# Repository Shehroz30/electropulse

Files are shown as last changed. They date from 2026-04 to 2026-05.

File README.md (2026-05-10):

# Electropulse

A custom, homemade, low voltage, simple TENs device
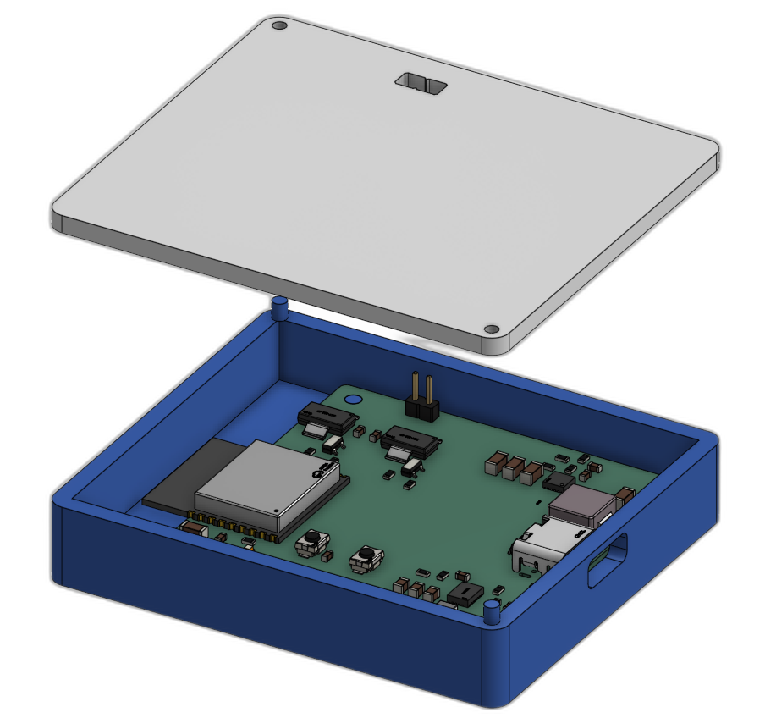
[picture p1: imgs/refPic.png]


## Features
* ESP32-C3 Microntroller with Bluetooth
* Wireless control
* WiFi controlled
* USB-C powered
* Low-cost - total BOM + board ~$11.56 per board
* Two output channels
* Modular + fits with different electrode types
* Two buck boosts for efficiency
* BJT controlled current limiter

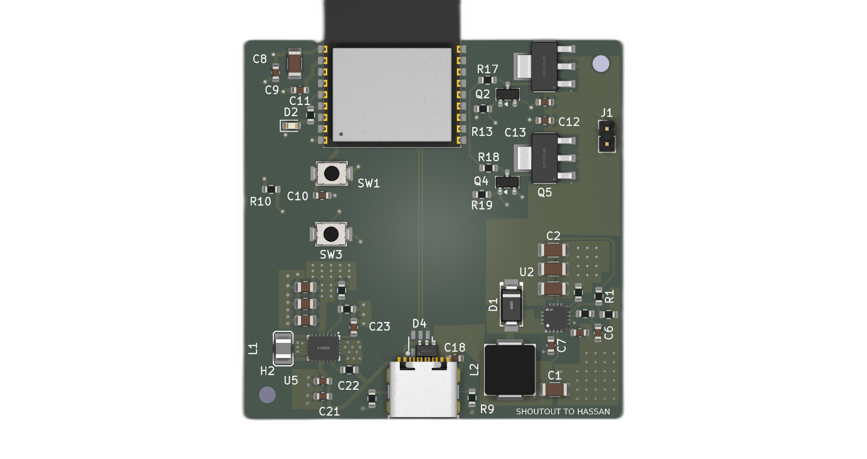
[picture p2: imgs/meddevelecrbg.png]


## Build
The build of this device is extremely uncomplicated. Use M3 0.5 inch screws for the enclosure and M2 0.315 inch screws for mounting the PCB. The electrodes can simply be attached to the Pin Headers.

A link to the Onshape file can be found [here](https://cad.onshape.com/documents/0b9b685ed737be4511598f4a/w/ba1d33f46afe7a8ff807ef53/e/736e59d6b3c7b8673a0b7fd8?renderMode=0&uiState=69ea24d6e717aaec3b4bf4c2)

## Use
* Flash the code onto the ESP32 using Arduino IDE
* Go to http://\<ESP-32\_IP\>/
* Connect your electrodes to the pin headers

## Motivation
I made this project because I've been struggling a little bit with knee pain and I found that other options on the market weren't as adjustable. I also had electrodes lying around (due to a separate business pitch project) and I wanted to make use of them

## BOM
To use this device, electrodes are a requirement. To purchase these, you can go to Amazon at [this link](https://www.amazon.com/Best-Sellers-Electrodes/zgbs/industrial/3013606011)
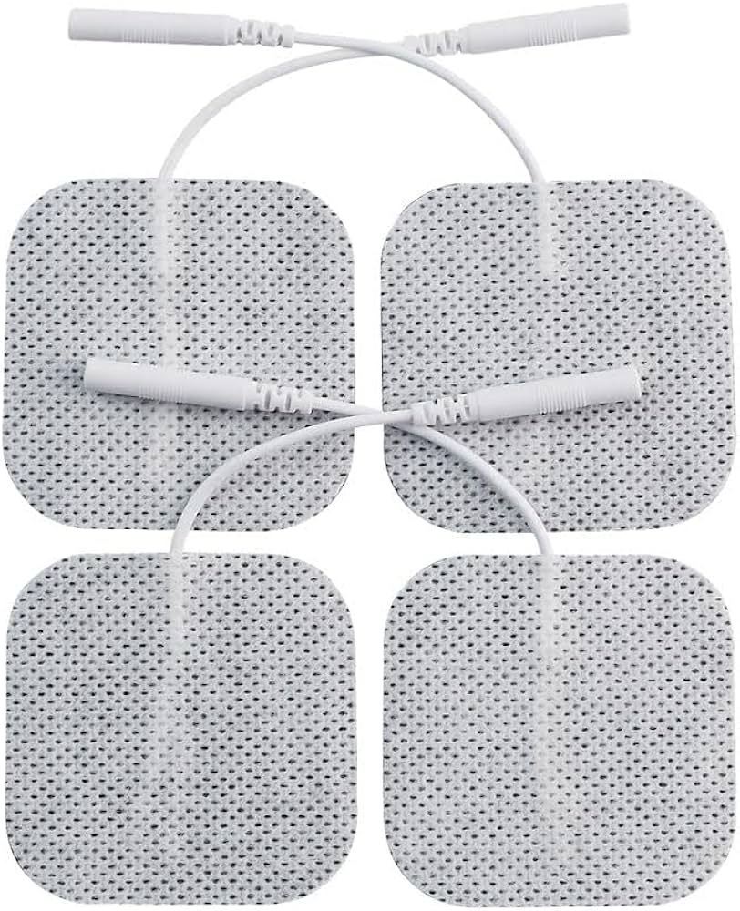
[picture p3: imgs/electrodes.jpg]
Electrodes


| Designator               | Footprint       |   Quantity | Value                | LCSC Part   | Link                                               |
|:-------------------------|:----------------|-----------:|:---------------------|:------------|:---------------------------------------------------|
| C1,C2,C3,C4              | 1206            |          8 | 4.7uF                | C29823      | https://www.lcsc.com/product-detail/C29823.html    |
| C5                       | 0603            |          2 | 0.047uF              | C1622       | https://www.lcsc.com/product-detail/C1622.html     |
| C8                       | 1206            |          2 | 10uF                 | C13585      | https://www.lcsc.com/product-detail/C13585.html    |
| C10,C11,C12,C13,C6,C7,C9 | 0603            |         18 | 0.1uF                | C14663      | https://www.lcsc.com/product-detail/C14663.html    |
| C18,C23                  | 0603            |        4   | 100nf                | C14663      | https://www.lcsc.com/product-detail/C14663.html    |
| C21,C22                  | 0605            |          4 | 10uf                 | C19702      | https://www.lcsc.com/product-detail/C19702.html    |
| C25,C26,C27              | 0805            |          6 | 22uf                 | C45783      | https://www.lcsc.com/product-detail/C45783.html    |
| D1                       | SMA(DO-214AC)   |          2 | D_Schottky           | C8678       | https://www.lcsc.com/product-detail/C8678.html     |
| D2                       | 0603            |          2 | LED                  | C2290       | https://www.lcsc.com/product-detail/C2290.html     |
| D4                       | SOT-23-6L       |          5 | USBLC6-2SC6          | C7519       | https://www.lcsc.com/product-detail/C7519.html     |
| J1                       | 插件,P=2.54mm     |          4 | Conn_01x02           | C32713268   | https://www.lcsc.com/product-detail/C32713268.html |
| J5                       | SMD             |          5 | MC-311D              | C136423     | https://www.lcsc.com/product-detail/C136423.html   |
| L1                       | 1008            |          5 | 2.2uH                | C86092      | https://www.lcsc.com/product-detail/C86092.html    |
| L2                       | SMD,7.2x6.6mm   |          5 | 10uH                 | C5189958    | https://www.lcsc.com/product-detail/C5189958.html  |
| Q2,Q4                    | SOT-23          |         10 | MMBT2222A            | C7420351    | https://www.lcsc.com/product-detail/C7420351.html  |
| Q3,Q5                    | SOT-223         |          5 | FZT853TA             | C435890     | https://www.lcsc.com/product-detail/C435890.html   |
| R1                       | 0603            |          2 | 250k                 | C22961      | https://www.lcsc.com/product-detail/C22961.html    |
| R2                       | 0603            |          2 | 330                  | C23138      | https://www.lcsc.com/product-detail/C23138.html    |
| R6                       | 0603            |          2 | 75k                  | C23242      | https://www.lcsc.com/product-detail/C23242.html    |
| R7                       | 0603            |          2 | 2k                   | C22975      | https://www.lcsc.com/product-detail/C22975.html    |
| R10,R14,R3               | 0603            |          6 | 10k                  | C25804      | https://www.lcsc.com/product-detail/C25804.html    |
| R11,R9                   | 0603            |          4 | 5.1k                 | C23186      | https://www.lcsc.com/product-detail/C23186.html    |
| R13,R19                  | 0603            |          4 | 14                   | C22950      | https://www.lcsc.com/product-detail/C22950.html    |
| R15                      | 0603            |          2 | 1M                   | C22935      | https://www.lcsc.com/product-detail/C22935.html    |
| R16                      | 0603            |         20 | 180k                 | C22827      | https://www.lcsc.com/product-detail/C22827.html    |
| R17,R18                  | 0603            |          4 | 1K                   | C21190      | https://www.lcsc.com/product-detail/C21190.html    |
| SW1,SW3                  | SMD,4x3mm       |          4 | TS-1088-AR02016      | C720477     | https://www.lcsc.com/product-detail/C720477.html   |
| U1                       | VFQFN-32-EP     |          2 | ESP32-C3-WROOM-02-N4 | C2934560    | https://www.lcsc.com/product-detail/C2934560.html  |
| U2                       | WQFN-16-EP(3x3) |          2 | TPS55340RTER         | C169167     | https://www.lcsc.com/product-detail/C169167.html   |
| U5                       | VSON-14-EP(3x4) |          2 | TPS63020DSJR         | C15483      | https://www.lcsc.com/product-detail/C15483.html    |

## JLCBPCB Order
For two assembled PCBs, the cost is around ~70$ for the cheapest shipping option. Keep in mind that there are a lot of alternatives to the parts selected, so ifsomething is unavailable you can easily change them around within the JLCPCB assembly order.
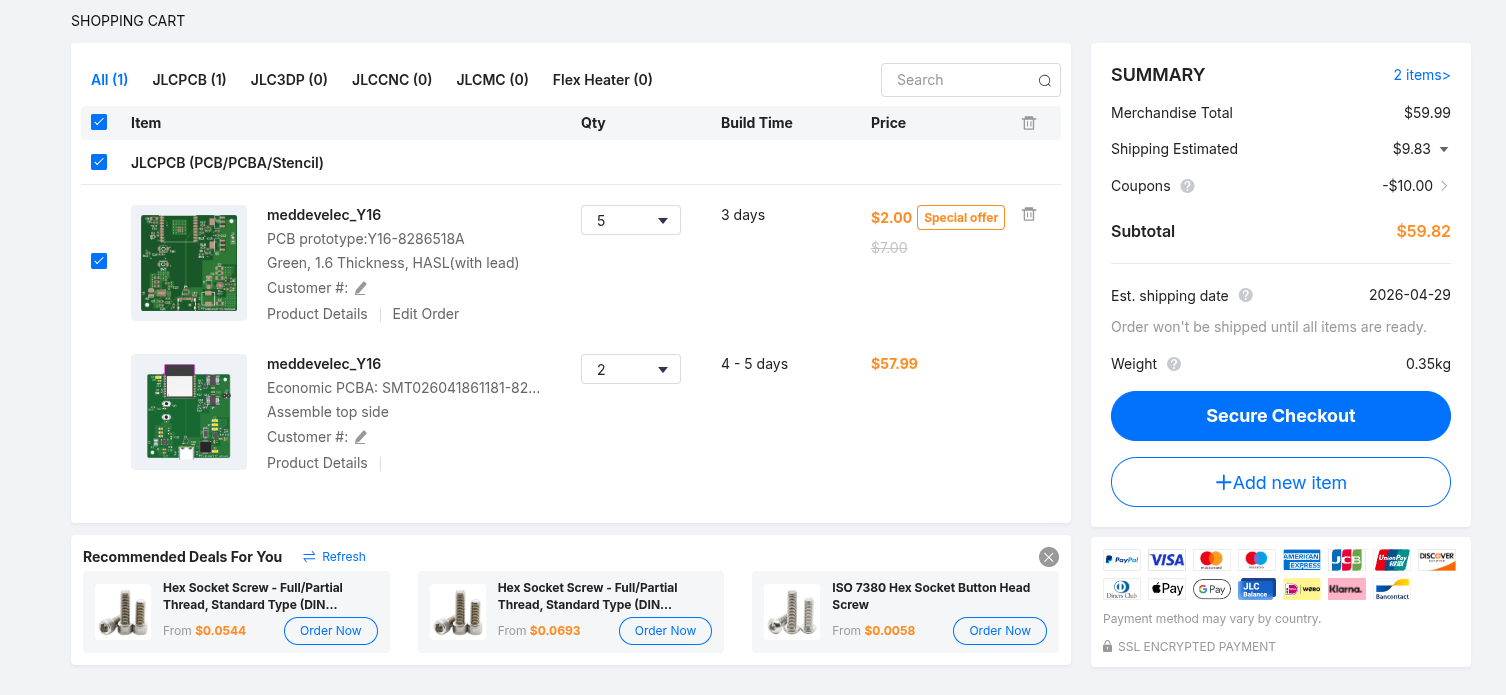
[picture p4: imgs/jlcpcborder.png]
Order


## Firmware

The code is written using Arduino IDE compiled for an ESP32-C3. Please note that the local host where the web page is hosted depends entirely on your ESP32, so it may not be the same for everyone. Also be sure to input your wifi credentials when flashing so that the ESP32 can connect to WiFi. 

## Fallout Zine Poster

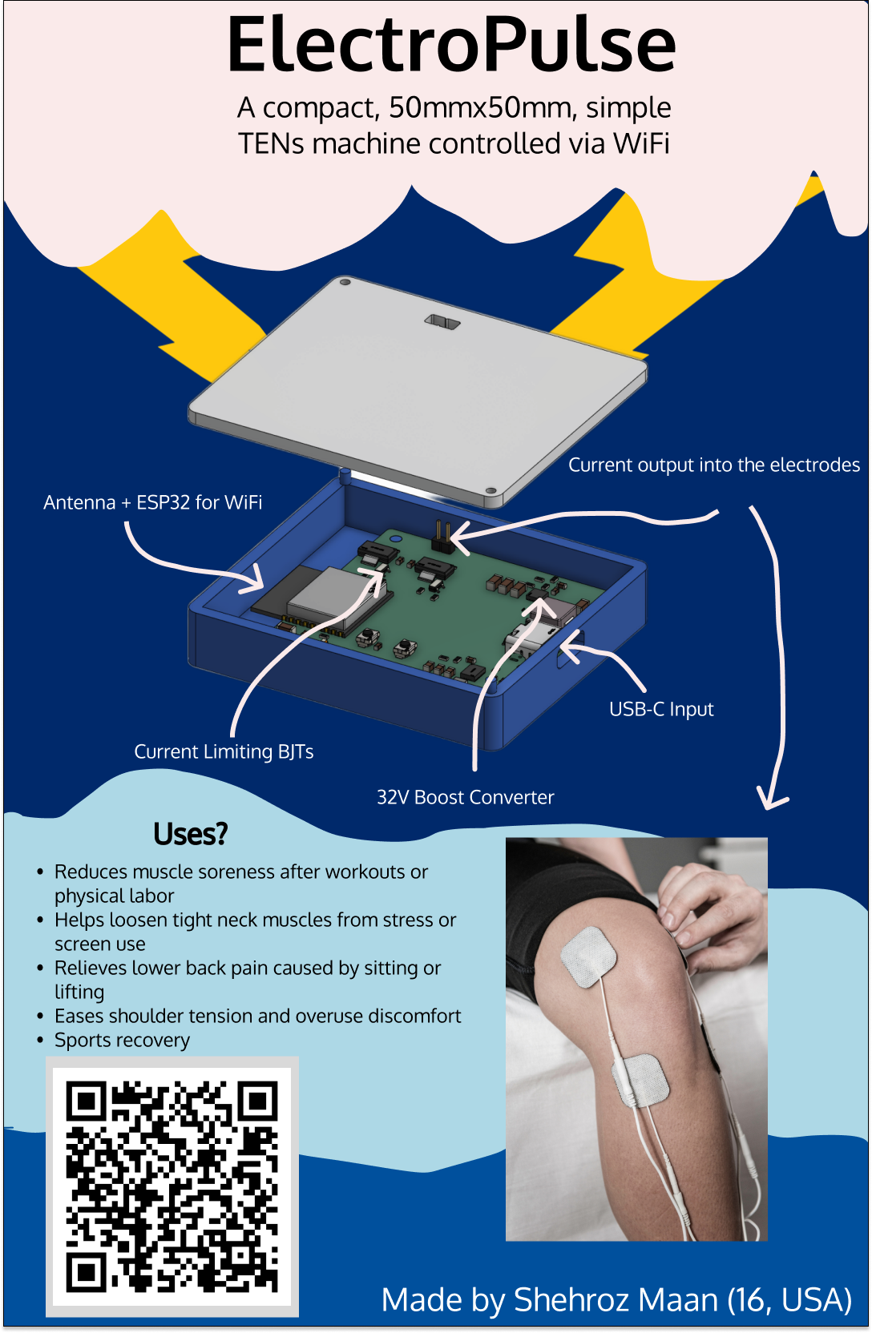
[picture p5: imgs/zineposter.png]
Zine Poster


## Thanks

Huge thanks to HackClub for helping me with this project!

## Verfication
Hack Club Username: shehrozmaan4

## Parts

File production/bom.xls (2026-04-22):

JLCPCB BOM Tool - BOM Matching
BOM name：medtechprojbo-JLCPCB Assembly Order.xlsx |  |  | Download Time：2026-04-19 00:56:08 |  |  |  | * Our matching results are updated in real-time, but stock and prices may change. If it's been over 24 hours, please re-match before placing your order.
PCB Assembled Qty：5 |  |  | Est. Total Price：18.6243
Your BOM |  |  |  |  | Matched Parts |  |  |  |  |  |  | Order Information
Top Designator | Bottom Designator | Comment | Footprint | JLCPCB Part # | Matches | Part # | Manufacturer | Footprint | Description | Category | Warning | JLCPCB Part # | Product link | Lib Type | Qty | Source | Total Price ($)
C1,C2,C3,C4 |  | 4.7uF | 1206 |  | Select by System | 1206B475K500NT | FH (Guangdong Fenghua Advanced Tech) | 1206 | 4.7uF 50V X7R ±10% 1206 Multilayer Ceramic Capacitors MLCC - SMD/SMT ROHS | Multilayer Ceramic Capacitors MLCC - SMD/SMT |  | C29823 | https://jlcpcb.com/partdetail/30577-1206B475K500NT/C29823 | Basic | 8 | 8 JLCPCB | 0.3152
C5 |  | 0.047uF | 0603 |  | Select by System | CL10B473KB8NNNC | Samsung Electro-Mechanics | 0603 | 47nF 50V X7R ±10% 0603 Multilayer Ceramic Capacitors MLCC - SMD/SMT ROHS | Multilayer Ceramic Capacitors MLCC - SMD/SMT |  | C1622 | https://jlcpcb.com/partdetail/1974-CL10B473KB8NNNC/C1622 | Basic | 2 | 2 JLCPCB | 0.0106
C8 |  | 10uF | 1206 |  | Select by System | CL31A106KBHNNNE | Samsung Electro-Mechanics | 1206 | 10uF 50V X5R ±10% 1206 Multilayer Ceramic Capacitors MLCC - SMD/SMT ROHS | Multilayer Ceramic Capacitors MLCC - SMD/SMT |  | C13585 | https://jlcpcb.com/partdetail/14236-CL31A106KBHNNNE/C13585 | Basic | 2 | 2 JLCPCB | 0.1244
C10,C11,C12,C13,C6,C7,C9 |  | 0.1uF | 0603 |  | Unconfirmed | CC0603KRX7R9BB104 | YAGEO | 0603 | 100nF 50V X7R ±10% 0603 Multilayer Ceramic Capacitors MLCC - SMD/SMT ROHS | Multilayer Ceramic Capacitors MLCC - SMD/SMT | 1.Multiple lines in the BOM have been matched to the same part. Please check if the matching is correct. ; | C14663 | https://jlcpcb.com/partdetail/YAGEO-CC0603KRX7R9BB104/C14663 | Basic | 18 | 18 JLCPCB | 0.0558
C18,C23 |  | 100nf | 0603 |  | Unconfirmed | CC0603KRX7R9BB104 | YAGEO | 0603 | 100nF 50V X7R ±10% 0603 Multilayer Ceramic Capacitors MLCC - SMD/SMT ROHS | Multilayer Ceramic Capacitors MLCC - SMD/SMT | 1.Multiple lines in the BOM have been matched to the same part. Please check if the matching is correct. ; | C14663 | https://jlcpcb.com/partdetail/YAGEO-CC0603KRX7R9BB104/C14663 | Basic | 18 | 18 JLCPCB | 0.0558
C21,C22 |  | 10uf | 0603 |  | Select by System | CL10A106KP8NNNC | Samsung Electro-Mechanics | 0603 | 10V 10uF X5R ±10% 0603 Multilayer Ceramic Capacitors MLCC - SMD/SMT ROHS | Multilayer Ceramic Capacitors MLCC - SMD/SMT |  | C19702 | https://jlcpcb.com/partdetail/20411-CL10A106KP8NNNC/C19702 | Basic | 4 | 4 JLCPCB | 0.032
C25,C26,C27 |  | 22uf | 0805 |  | Select by System | CL21A226MAQNNNE | Samsung Electro-Mechanics | 0805 | 22uF 25V X5R ±20% 0805 Multilayer Ceramic Capacitors MLCC - SMD/SMT ROHS | Multilayer Ceramic Capacitors MLCC - SMD/SMT |  | C45783 | https://jlcpcb.com/partdetail/46786-CL21A226MAQNNNE/C45783 | Basic | 6 | 6 JLCPCB | 0.1914
D1 |  | D_Schottky | SMA(DO-214AC) |  | Select by System | SS34 | MDD(Microdiode Semiconductor) | SMA(DO-214AC) | -55℃~+125℃ 3A 40V 500uA@40V 550mV@3A Independent SMA(DO-214AC) Schottky Diodes ROHS | Schottky Diodes |  | C8678 | https://jlcpcb.com/partdetail/MDD_Microdiode_Semiconductor-SS34/C8678 | Basic | 2 | 2 JLCPCB | 0.0596
D2 |  | LED | 0603 |  | Select by System | KT-0603W | Hubei KENTO Elec | 0603 | -40℃~+85℃ 100mW 120° 2.6V~3.1V 360mcd 5mA Discrete Diode Top-mount White Yellow Lens 0603 LED Indication - Discrete ROHS | LED Indication - Discrete |  | C2290 | https://jlcpcb.com/partdetail/Hubei_KENTOElec-KT0603W/C2290 | Basic | 2 | 2 JLCPCB | 0.024
D4 |  | USBLC6-2SC6 | SOT-23-6L |  | Select by System | USBLC6-2SC6 | STMicroelectronics | SOT-23-6L | -40℃~+125℃ 150nA 17V 2 3.5pF 5.25V 5A 6V ESD IEC 61000-4-2 Unidirectional SOT-23-6L ESD and Surge Protection (TVS/ESD) ROHS | ESD And Surge Protection (TVS/ESD) |  | C7519 | https://jlcpcb.com/partdetail/STMicroelectronics-USBLC62SC6/C7519 | Extended | 5 | 5 JLCPCB | 0.7245
J1 |  | Conn_01x02 | 插件,P=2.54mm |  | Select by System | HX PZ2.54-1x2P ZZ | hanxia | 插件,P=2.54mm | -40℃~+105℃ 1 1kV 1x2P 2.54mm 2.5mm 2P 3A 3mm 6mm Black Brass Gold Pin Header Through Hole Plugin,P=2.54mm Pin Headers ROHS | Pin Headers |  | C32713268 | https://jlcpcb.com/partdetail/hanxia-HX_PZ2_54_1x2PZZ/C32713268 | Extended | 4 | 4 JLCPCB | 0.0628
J5 |  | MC-311D | SMD |  | Select by System | MC-311D | SOFNG | SMD | -35℃~+75℃ 1 12V 16P 5A 7.35mm 8,000 times、10000 times Black Female Surface Mount, Right Angle Type-C SMD USB Connectors ROHS | USB Connectors |  | C136423 | https://jlcpcb.com/partdetail/SOFNG-MC311D/C136423 | Extended | 5 | 5 JLCPCB | 1.1375
L1 |  | 2.2uH | 1008 |  | Select by System | LQM2HPN2R2MG0L | Murata Electronics | 1008 | 1.3A 100mΩ 2.2uH 40MHz ±20% 1008 Inductors (SMD) ROHS | Inductors (SMD) |  | C86092 | https://jlcpcb.com/partdetail/MurataElectronics-LQM2HPN2R2MG0L/C86092 | Extended | 5 | 5 JLCPCB | 0.4515
L2 |  | 10uH | SMD,7.2x6.6mm |  | Select by System | CYA0630-10UH | SHOU HAN | SMD,7.2x6.6mm | 10uH 4A 5.5A 71mΩ ±20% SMD,7.2x6.6mm Inductors (SMD) ROHS | Inductors (SMD) |  | C5189958 | https://jlcpcb.com/partdetail/SHOUHAN-CYA063010UH/C5189958 | Extended | 5 | 5 JLCPCB | 0.763
Q2,Q4 |  | MMBT2222A | SOT-23 |  | Select by System | MMBT2222A | hongjiacheng | SOT-23 | -55℃~+150℃ 1 NPN 100 100nA 1V 300MHz 300mW 40V 600mA 6V NPN SOT-23 Bipolar (BJT) ROHS | Bipolar (BJT) |  | C7420351 | https://jlcpcb.com/partdetail/hongjiacheng-MMBT2222A/C7420351 | Extended | 10 | 10 JLCPCB | 0.152
Q3,Q5 |  | FZT853TA | SOT-223 |  | Select by System | FZT853TA | Diodes Incorporated | SOT-223 | -55℃~+150℃ 1 NPN 100 100V 10nA 130MHz 150mV 3W 6A 7V NPN SOT-223 Bipolar (BJT) ROHS | Bipolar (BJT) |  | C435890 | https://jlcpcb.com/partdetail/DiodesIncorporated-FZT853TA/C435890 | Extended | 5 | 5 JLCPCB | 4.106
R1 |  | 250k | 0603 |  | Select by System | 0603WAF2203T5E | UNI-ROYAL(Uniroyal Elec) | 0603 | -55℃~+155℃ 100mW 220kΩ 75V Thick Film Resistor ±1% ±100ppm/℃ 0603 Chip Resistor - Surface Mount ROHS | Chip Resistor - Surface Mount |  | C22961 | https://jlcpcb.com/partdetail/23688-0603WAF2203T5E/C22961 | Basic | 2 | 2 JLCPCB | 0.0032
R2 |  | 330 | 0603 |  | Select by System | 0603WAF3300T5E | UNI-ROYAL(Uniroyal Elec) | 0603 | -55℃~+155℃ 100mW 330Ω 75V Thick Film Resistor ±1% ±100ppm/℃ 0603 Chip Resistor - Surface Mount ROHS | Chip Resistor - Surface Mount |  | C23138 | https://jlcpcb.com/partdetail/23865-0603WAF3300T5E/C23138 | Basic | 2 | 2 JLCPCB | 0.0032
R6 |  | 75k | 0603 |  | Select by System | 0603WAF7502T5E | UNI-ROYAL(Uniroyal Elec) | 0603 | -55℃~+155℃ 100mW 75V 75kΩ Thick Film Resistor ±1% ±100ppm/℃ 0603 Chip Resistor - Surface Mount ROHS | Chip Resistor - Surface Mount |  | C23242 | https://jlcpcb.com/partdetail/23969-0603WAF7502T5E/C23242 | Basic | 2 | 2 JLCPCB | 0.0032
R7 |  | 2k | 0603 |  | Select by System | 0603WAF2001T5E | UNI-ROYAL(Uniroyal Elec) | 0603 | -55℃~+155℃ 100mW 2kΩ 75V Thick Film Resistor ±1% ±100ppm/℃ 0603 Chip Resistor - Surface Mount ROHS | Chip Resistor - Surface Mount |  | C22975 | https://jlcpcb.com/partdetail/23702-0603WAF2001T5E/C22975 | Basic | 2 | 2 JLCPCB | 0.0034
R10,R14,R3 |  | 10k | 0603 |  | Select by System | 0603WAF1002T5E | UNI-ROYAL(Uniroyal Elec) | 0603 | -55℃~+155℃ 100mW 10kΩ 75V Thick Film Resistor ±1% ±100ppm/℃ 0603 Chip Resistor - Surface Mount ROHS | Chip Resistor - Surface Mount |  | C25804 | https://jlcpcb.com/partdetail/26547-0603WAF1002T5E/C25804 | Basic | 6 | 6 JLCPCB | 0.0084
R11,R9 |  | 5.1k | 0603 |  | Select by System | 0603WAF5101T5E | UNI-ROYAL(Uniroyal Elec) | 0603 | -55℃~+155℃ 100mW 5.1kΩ 75V Thick Film Resistor ±1% ±100ppm/℃ 0603 Chip Resistor - Surface Mount ROHS | Chip Resistor - Surface Mount |  | C23186 | https://jlcpcb.com/partdetail/23913-0603WAF5101T5E/C23186 | Basic | 4 | 4 JLCPCB | 0.0064
R13,R19 |  | 14 | 0603 |  | Select by System | 0603WAF200JT5E | UNI-ROYAL(Uniroyal Elec) | 0603 | -55℃~+155℃ 100mW 20Ω 75V Thick Film Resistor ±1% ±100ppm/℃ 0603 Chip Resistor - Surface Mount ROHS | Chip Resistor - Surface Mount |  | C22950 | https://jlcpcb.com/partdetail/23677-0603WAF200JT5E/C22950 | Basic | 4 | 4 JLCPCB | 0.0064
R15 |  | 1M | 0603 |  | Select by Customer | 0603WAF1004T5E | UNI-ROYAL(Uniroyal Elec) | 0603 | -55℃~+155℃ 100mW 1MΩ 75V Thick Film Resistor ±1% ±100ppm/℃ 0603 Chip Resistor - Surface Mount ROHS | Chip Resistor - Surface Mount |  | C22935 | https://jlcpcb.com/partdetail/23662-0603WAF1004T5E/C22935 | Basic | 2 | 2 JLCPCB | 0.003
R16 |  | 180k | 0603 |  | Select by Customer | 0603WAF1803T5E | UNI-ROYAL(Uniroyal Elec) | 0603 | -55℃~+155℃ 100mW 180kΩ 75V Thick Film Resistor ±1% ±100ppm/℃ 0603 Chip Resistor - Surface Mount ROHS | Chip Resistor - Surface Mount |  | C22827 | https://jlcpcb.com/partdetail/23554-0603WAF1803T5E/C22827 | Extended | 20 | 20 JLCPCB | 0.03
R17,R18 |  | 1K | 0603 |  | Select by System | 0603WAF1001T5E | UNI-ROYAL(Uniroyal Elec) | 0603 | -55℃~+155℃ 100mW 1kΩ 75V Thick Film Resistor ±1% ±100ppm/℃ 0603 Chip Resistor - Surface Mount ROHS | Chip Resistor - Surface Mount |  | C21190 | https://jlcpcb.com/partdetail/21904-0603WAF1001T5E/C21190 | Basic | 4 | 4 JLCPCB | 0.0064
SW1,SW3 |  | TS-1088-AR02016 | SMD,4x3mm |  | Select by System | TS-1088-AR02016 | XUNPU | SMD,4x3mm | -30℃~+80℃ 1.6N 100,000 cycles 12V 2mm 3mm 4mm 50mA Black Round Button SMD(SMT) Tab SPST Surface Mount,Vertical Without Bracket SMD,4x3mm Tactile Switches ROHS | Tactile Switches |  | C720477 | https://jlcpcb.com/partdetail/XUNPU-TS_1088AR02016/C720477 | Basic | 4 | 4 JLCPCB | 0.2224
U1 |  | ESP32-C3-WROOM-02-N4 | VFQFN-32-EP |  | Select by System | ESP32-C3-WROOM-02-N4 | Espressif Systems | VFQFN-32-EP | -105dBm -40℃~+85℃ 2.4GHz 20.5dBm 345mA 3V~3.6V 82mA Bluetooth5.0 ESP32-C3 Chip On-board PCB Antenna UART、SPI、I2C、I2S、JTAG、USB VFQFN-32-EP WiFi Modules ROHS | WiFi Modules |  | C2934560 | https://jlcpcb.com/partdetail/3281215-ESP32_C3_WROOM_02N4/C2934560 | Extended | 2 | 2 JLCPCB | 6.2748
U2 |  | TPS55340RTER | WQFN-16-EP(3x3) |  | Select by System | TPS55340RTER | Texas Instruments | WQFN-16-EP(3x3) | -40℃~+125℃@(TA) 1 1.14MHz 2.9V~32V 2.9V~38V 5.25A 500uA Adjustable Boost Boost、SEPIC、Flyback Built-in No WQFN-16-EP(3x3) DC-DC Converters ROHS | DC-DC Converters |  | C169167 | https://jlcpcb.com/partdetail/TexasInstruments-TPS55340RTER/C169167 | Extended | 2 | 2 JLCPCB | 1.985
U5 |  | TPS63020DSJR | VSON-14-EP(3x4) |  | Select by System | TPS63020DSJR | Texas Instruments | VSON-14-EP(3x4) | -40℃~+85℃@(TA) 1 1.2V~5.5V 1.8V~5.5V 2.4MHz 3A 50uA Adjustable Buck-Boost Buck-Boost Built-in Yes VSON-14-EP(3x4) DC-DC Converters ROHS | DC-DC Converters |  | C15483 | https://jlcpcb.com/partdetail/TexasInstruments-TPS63020DSJR/C15483 | Extended | 2 | 2 JLCPCB | 1.8024

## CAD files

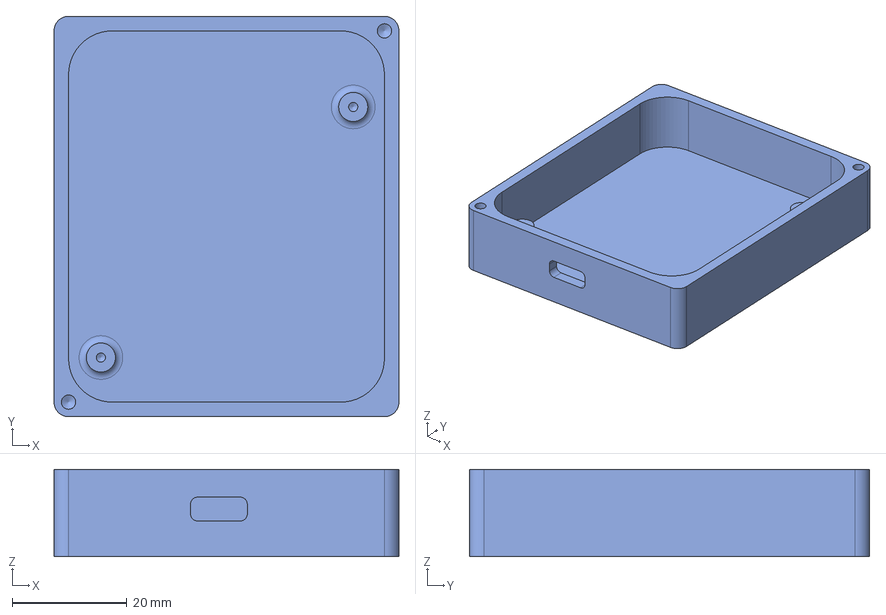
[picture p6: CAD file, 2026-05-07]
3Dmodel/enclosure_body.step
60.2 x 69.8 x 15.2 mm

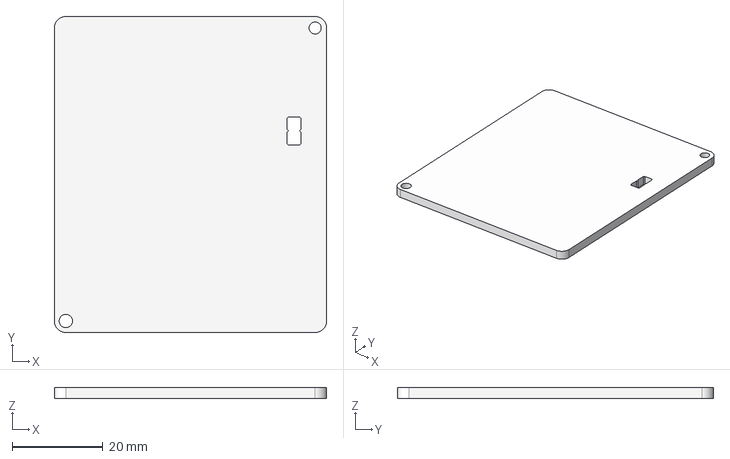
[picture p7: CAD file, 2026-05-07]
3Dmodel/enclosure_cover.step
60.2 x 69.8 x 2.54 mm

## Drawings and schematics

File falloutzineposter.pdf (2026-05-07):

# ElectroPulse

## A compact, 50mmx50mm, simple

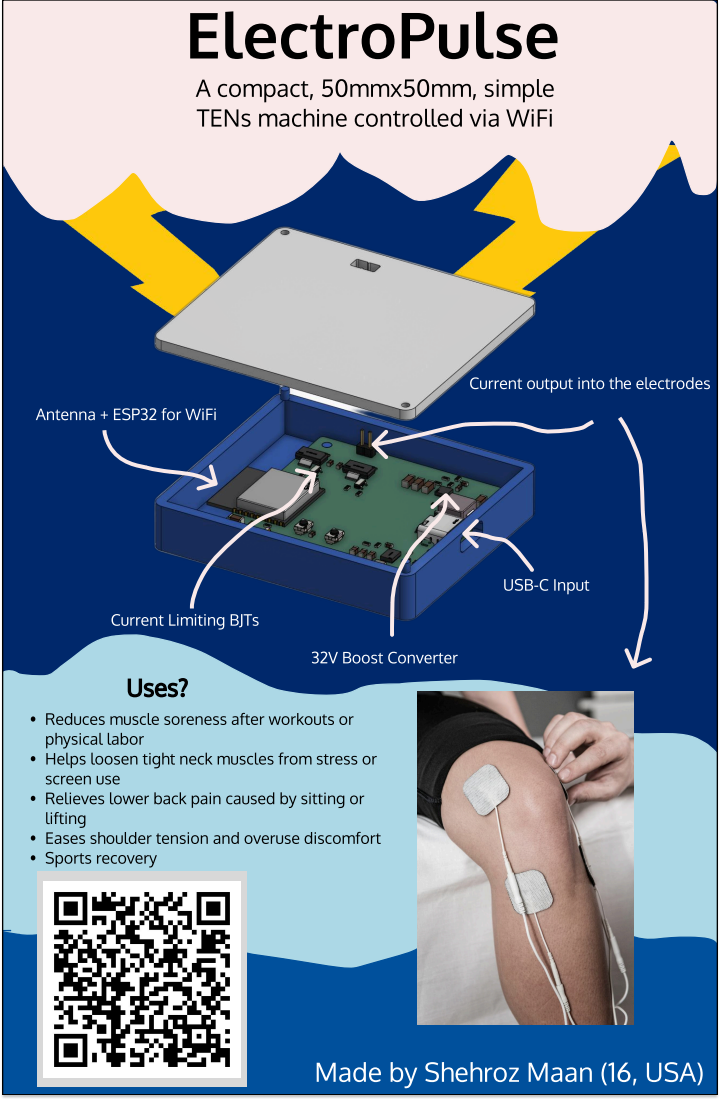
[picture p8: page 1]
USB-C Input; 32V Boost Converter; Uses?

TENs machine controlled via WiFi

Current output into the electrodes

Antenna + ESP32 for WiFi

Current Limiting BJTs

Reduces muscle soreness after workouts or
physical labor
Helps loosen tight neck muscles from stress or
screen use
Relieves lower back pain caused by sitting or
lifting
Eases shoulder tension and overuse discomfort
Sports recovery

Made by Shehroz Maan (16, USA)

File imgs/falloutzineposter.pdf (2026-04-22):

# ElectroPulse

## A compact, 50mmx50mm, simple

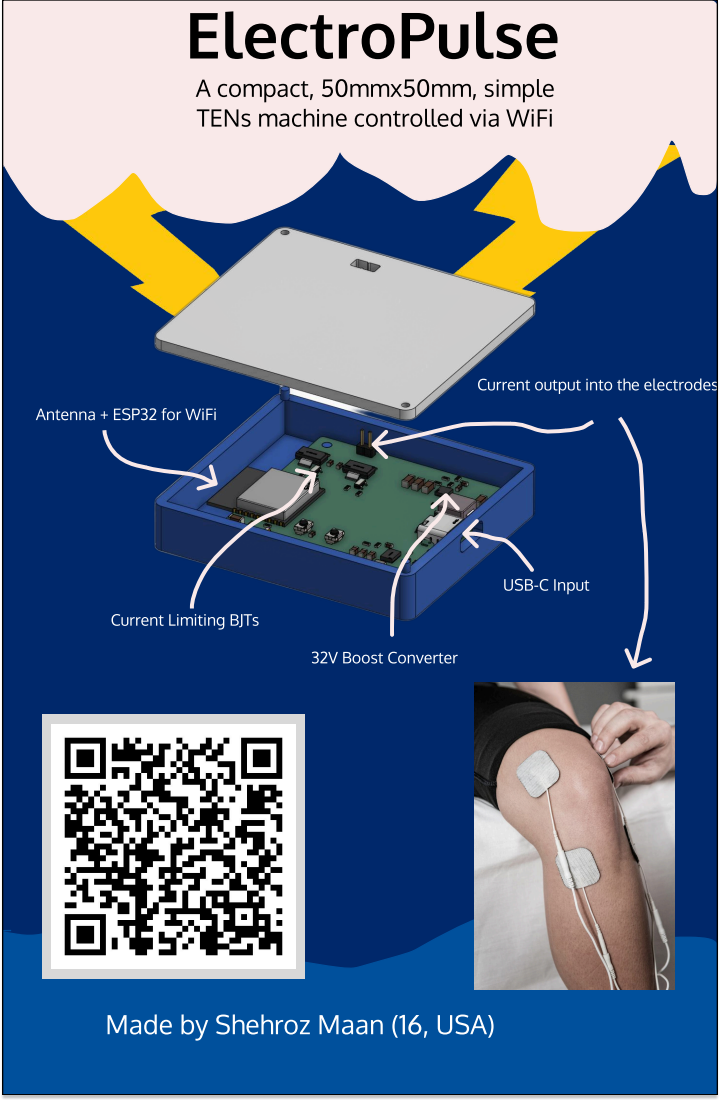
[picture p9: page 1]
USB-C Input; 32V Boost Converter

TENs machine controlled via WiFi

Current output into the electrodes

Antenna + ESP32 for WiFi

Current Limiting BJTs

Made by Shehroz Maan (16, USA)

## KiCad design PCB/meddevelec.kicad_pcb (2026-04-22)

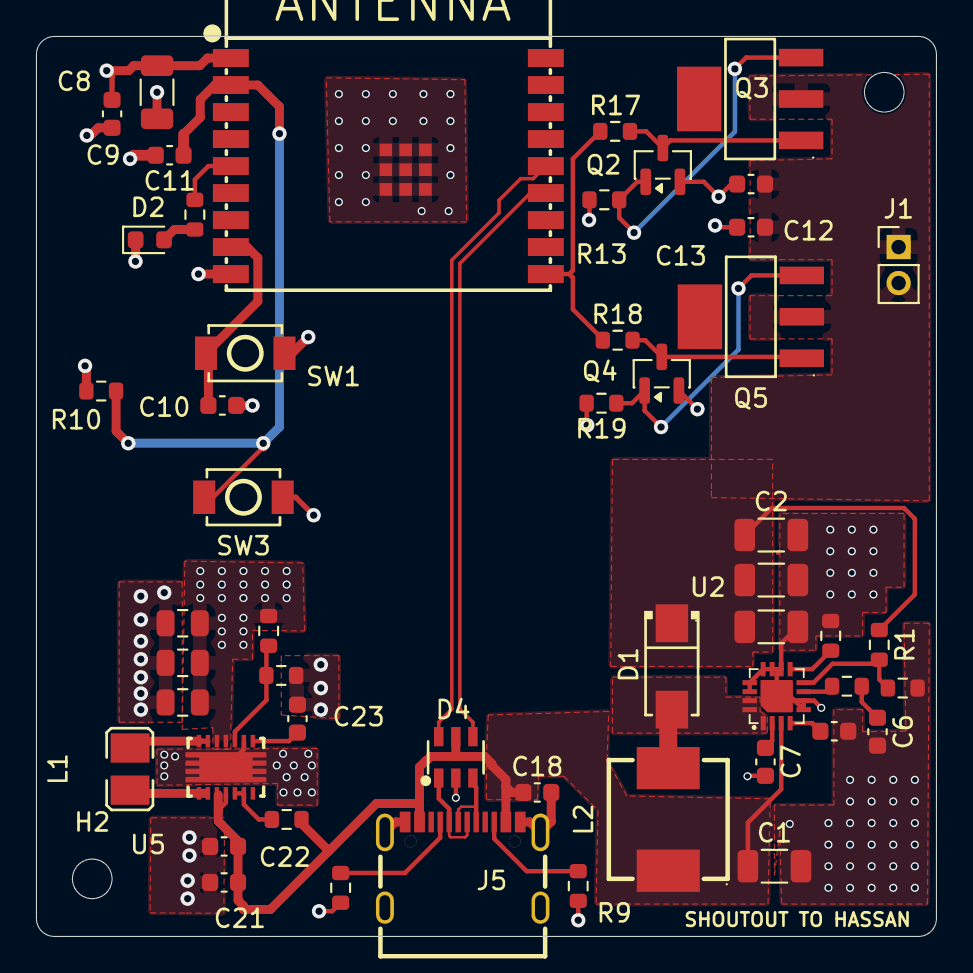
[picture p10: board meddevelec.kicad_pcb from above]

Board: 4 copper layers, 50.0 x 50.0 mm, 55 parts (0 on the bottom side), 31 nets.

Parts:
C1, C2, C3, C4: 4.7uF; C_1206_3216Metric
C5: 0.047uF; C_0603_1608Metric
C6, C7, C9, C10, C11, C12, C13: 0.1uF; C_0603_1608Metric
C8: 10uF; C_1206_3216Metric
C18, C23: 100nf; C_0603_1608Metric
C21, C22: 10uf; C_0603_1608Metric
C25, C26, C27: 22uf; C_0805_2012Metric
D1: D_Schottky; SMA_L4.3-W2.7-LS5.1-RD
D2: LED; LED_0603_1608Metric
D4: USBLC6-2SC6; SOT-23-6_L2.9-W1.6-P0.95-LS2.8-BL
H1, H2, H3, H4: MountingHole; MountingHole_2.2mm_M2
J1: Conn_01x02; PinHeader_1x02_P2.00mm_Vertical
J5: MC-311D; USB-C-SMD_MC-311D
L1: 2.2uH; L1008
L2: 10uH; IND-SMD_L7.2-W6.6_GPSR07X0
Q2, Q4: MMBT2222A; SOT-23
Q3, Q5: FZT853TA; SOT-223-4_L6.5-W3.5-P2.30-LS7.0-BR
R1: 250k; R_0603_1608Metric
R2: 330; R_0603_1608Metric
R3, R10, R14: 10k; R_0603_1608Metric
R6: 75k; R_0603_1608Metric
R7: 2k; R_0603_1608Metric
R9, R11: 5.1k; R_0603_1608Metric
R13, R19: 14; R_0603_1608Metric
R15: 1M; R_0603_1608Metric
R16: 180k; R_0603_1608Metric
R17, R18: 1K; R_0603_1608Metric
SW1, SW3: TS-1088-AR02016; SW-SMD_L3.9-W3.0-P4.45
U1: ESP32-C3-WROOM-02-N4; BULETM-SMD_ESPRESSIF_ESP32-C3-WROOM-02-N4-4MB
U2: TPS55340RTER; VQFN-16_L3.0-W3.0-P0.50-BL-EP1.7
U5: TPS63020DSJR; VSON-14_L4.0-W3.0-P0.50-BL-EP_TI_DSJ

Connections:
+3.3V: C8.1, C9.1, C25.1, C26.1, C27.1, R10.1, R15.1, U1.1 (3V3), U5.4 (VOUT), U5.5 (VOUT)
+5V: C1.1, C18.1, C21.1, C22.1, D4.5, J5.A4-B9 (VBUS), J5.B4-A9 (VBUS), L2.1, R14.2, U2.3 (EN), U5.10 (VIN), U5.11 (VIN)
+32V: C2.1, C3.1, C4.1, C12.1, C13.1, D1.1 (K), J1.1, J1.2, Q3.2 (C), Q5.2 (C), R1.1
/BOOT: C10.1, SW1.2, U1.8 (IO9)
/D+: D4.4, U1.13 (IO18)
/D-: D4.6, U1.14 (IO19)
/LED: R2.1, U1.5 (IO6)
/PWM_C: R17.1, R18.1, U1.10 (IO10)
/UD+: D4.3, J5.A6 (DP1), J5.B6 (DP2)
/UD-: D4.1, J5.A7 (DN1), J5.B7 (DN2)
GND: C1.2, C2.2, C3.2, C4.2, C5.2, C6.2, C7.2, C8.2, C9.2, C10.2, C11.2, C12.2, C13.2, C18.2, C21.2, C22.2, C23.2, C25.2, C26.2, C27.2, D2.1 (K), D4.2, J5.1 (SHIELD), J5.2 (SHIELD), J5.3 (SHIELD), J5.4 (SHIELD), J5.A1-B12 (GND), J5.B1-A12 (GND), Q2.2 (E), Q4.2 (E), R3.2, R6.2, R9.2, R11.2, R13.2, R16.2, R19.2, SW1.1, SW3.1, U1.9 (GND), U1.19 (EP), U2.5 (SYNC), U2.6 (AGND), U2.10 (NC), U2.11 (PGND), U2.12 (PGND), U2.13 (PGND), U2.14 (NC), U2.17 (EP), U5.2 (GND), U5.15 (PGND)
unnamed: C6.1, R7.2
unnamed: D1.2 (A), L2.2, U2.1 (SW), U2.15 (SW), U2.16 (SW)
unnamed: D2.2 (A), R2.2
unnamed: J5.A5 (CC1), R11.1
unnamed: J5.B5 (CC2), R9.1
unnamed: L1.1, U5.8 (L1), U5.9 (L1)
unnamed: L1.2, U5.6 (L2), U5.7 (L2)
unnamed: Q2.1 (B), Q3.3 (E), R13.1
unnamed: Q2.3 (C), Q3.1 (B), R17.2
unnamed: Q4.1 (B), Q5.3 (E), R19.1
unnamed: Q4.3 (C), Q5.1 (B), R18.2
unnamed: C11.1, R10.2, SW3.2, U1.2 (EN)
unnamed: R7.1, U2.7 (COMP)
unnamed: R1.2, R3.1, U2.8 (FB)
unnamed: R6.1, U2.9 (FREQ)
unnamed: C5.1, U2.4 (SS)
unnamed: C7.1, U2.2 (VIN)
unnamed: R14.1, U5.12 (EN), U5.13 (PS/SYNC)
unnamed: R15.2, R16.1, U5.3 (FB)
unnamed: C23.1, U5.1 (VINA)

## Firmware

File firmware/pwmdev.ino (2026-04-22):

#include <WiFi.h>
#include <WebServer.h>

// WiFi credentials
const char* ssid     = "YOUR_SSID";
const char* password = "YOUR_PASSWORD";

// GPIO assignments
#define LED_PIN 6
#define PWM_PIN 10

// PWM configuration (runtime adjustable frequency)
static int pwmFreq       = 100;   // Hz (default)
static const int pwmResolution = 10;  // 10-bit (0–1023)

// Duty values
static const int dutyOn  = 512;
static const int dutyOff = 0;

// HTTP server
WebServer server(80);

// State
static bool pwmEnabled = false;


// HTML page with frequency slider
void handleRoot()
{
    String page;
    page.reserve(512);

    page += "<!DOCTYPE html><html><head>";
    page += "<meta name='viewport' content='width=device-width, initial-scale=1'>";
    page += "<style>body{font-family:sans-serif;text-align:center;margin-top:40px;}";
    page += "button{padding:12px 24px;font-size:16px;margin:8px;}";
    page += "input{width:300px;}</style>";
    page += "</head><body>";

    page += "<h3>PWM Output</h3>";
    page += "<p>Status: ";
    page += (pwmEnabled ? "ON" : "OFF");
    page += "</p>";

    page += "<a href='/on'><button>ON</button></a>";
    page += "<a href='/off'><button>OFF</button></a>";

    page += "<p>Frequency: <span id='fval'>";
    page += String(pwmFreq);
    page += "</span> Hz</p>";

    page += "<input type='range' min='80' max='120' value='";
    page += String(pwmFreq);
    page += "' id='freq' oninput='updateFreq(this.value)'>";

    page += "<script>";
    page += "function updateFreq(val){";
    page += "document.getElementById('fval').innerText = val;";
    page += "fetch('/setFreq?f=' + val);";
    page += "}";
    page += "</script>";

    page += "</body></html>";

    server.send(200, "text/html", page);
}


// Enable PWM
void handleOn()
{
    pwmEnabled = true;
    ledcWrite(PWM_PIN, dutyOn);
    digitalWrite(LED_PIN, HIGH);

    server.sendHeader("Location", "/");
    server.send(303);
}


// Disable PWM
void handleOff()
{
    pwmEnabled = false;
    ledcWrite(PWM_PIN, dutyOff);
    digitalWrite(LED_PIN, LOW);

    server.sendHeader("Location", "/");
    server.send(303);
}


// Update frequency
void handleSetFreq()
{
    if (server.hasArg("f")) {
        pwmFreq = server.arg("f").toInt();

        // reattach with new frequency
        ledcDetach(PWM_PIN);
        ledcAttach(PWM_PIN, pwmFreq, pwmResolution);

        // restore state
        ledcWrite(PWM_PIN, pwmEnabled ? dutyOn : dutyOff);
    }

    server.send(200, "text/plain", "OK");
}


void setup()
{
    pinMode(LED_PIN, OUTPUT);
    digitalWrite(LED_PIN, LOW);

    // initial PWM setup
    ledcAttach(PWM_PIN, pwmFreq, pwmResolution);
    ledcWrite(PWM_PIN, dutyOff);

    WiFi.begin(ssid, password);
    while (WiFi.status() != WL_CONNECTED) {
        delay(200);
    }

    server.on("/", handleRoot);
    server.on("/on", handleOn);
    server.on("/off", handleOff);
    server.on("/setFreq", handleSetFreq);

    server.begin();
    Serial.println(WiFi.localIP());

}


void loop()
{
    server.handleClient();
}

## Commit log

2026-04-22 final parts commit
    [bom.csv, bom.xls, designators.csv, enclosure_body.step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]
2026-04-23 fixed bom + readme
    [bom.csv]
2026-04-23 fix bom
    [bom.csv]
2026-05-07 fix project requirements
    [enclosure_body.step, enclosure_cover.step]
